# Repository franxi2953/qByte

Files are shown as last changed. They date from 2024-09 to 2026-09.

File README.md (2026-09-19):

> **Original GitLab repository:** This project was originally published in the [qByte directory of Open Bioeconomy Lab's RT-LAMP device repository](https://gitlab.com/open-bioeconomy-lab/diagnostics-hardware/rt-lamp-device/-/tree/master/qByte?ref_type=heads).

# qByte

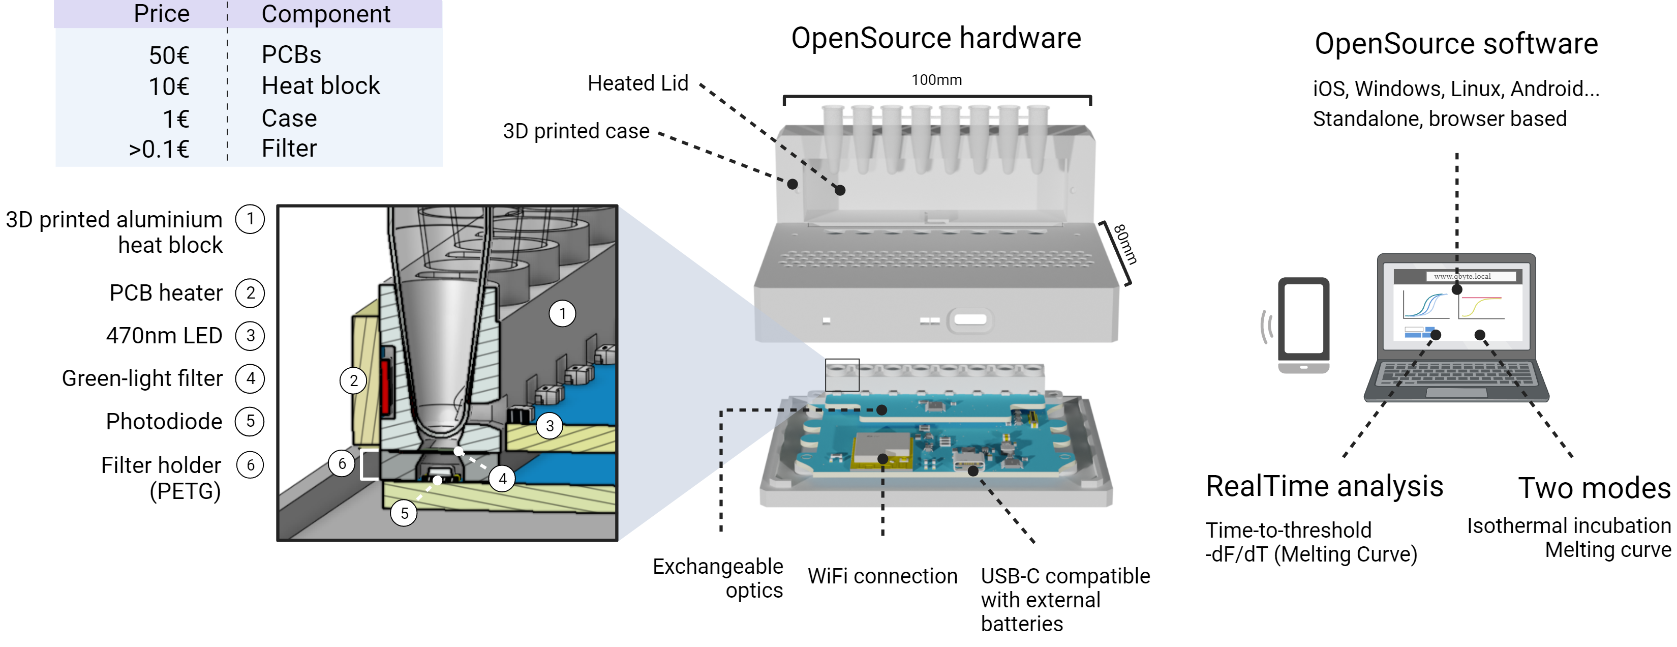
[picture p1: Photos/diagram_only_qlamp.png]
open_qLAMP


## Contents

- [Paper reference](#paper-reference)
- [Introduction](#introduction)
- [Quick start](#quick-start)
- [Making the device](#making-the-device)
- [Results](#results)
- [Components](#components)
  - [Costs](#costs)
  - [Electronics](#electronics)
  - [Code and firmware](#code-and-firmware)
  - [Case](#case)
- [Funding](#funding)
- [License](#license)

## Paper Reference

qByte: An open-source isothermal fluorimeter for democratizing analysis of nucleic acids, proteins and cells
Quero FJ, Aidelberg G, Vielfaure H, Huon de Kermadec Y, Cazaux S, et al. (2025) qByte: An open-source isothermal fluorimeter for democratizing analysis of nucleic acids, proteins and cells. PLOS Biology 23(5): e3003199. https://doi.org/10.1371/journal.pbio.3003199

## Introduction

Accessibility to scientific and diagnostic instrumentation is one of the main bottlenecks in the implementation of global health and decentralized science. The advancement of digital fabrication techniques and the cheapening of electronic prototyping have facilitated the emergence of open source prototypes that lower the cost of entry of these technologies. However, despite the importance of these prototypes for making the hands-on biotechnology more ubiquitous, they rarely move from the prototyping phase to their actual implementation, with their subsequent adaptation to mass production and validation in real scenarios. This is particularly relevant in the field of nucleic acid amplification, the gold standard in the field of diagnostics and biosensing. Despite relevant open-source products that allow nucleic acid amplification (as [PocketPCR](https://gaudi.ch/PocketPCR/) or [NinjaPCR](https://ninjapcr.tori.st/)) their results still require a subsequent analysis by electrophoresis gels or an end-point examination with a transilluminator. 

Here we describe the design and mid-scale production of the Open qLAMP, a device that, for a manufacturing cost of less than 50€, allows real-time detection of nucleic acid amplifications. We also include data that, together with our <2$ [in-house produced LAMP reactions](https://www.protocols.io/view/corona-detective-user-protocol-v2-0-14egnzbyqg5d/v2), validate the device for the detection of numerous targets, including SARS-CoV-2 clinical samples in resource constrained regions, presence of GMO elements in commercial food and the early detection of fungal infestation on chestnut plantations. Finally, we present results on how this system also has great potential in other fields such as enzyme activity characterization, protein production in cell-free extracts or antibiotic resistance screening in bacterial samples.

## Quick Start

This is a quick guide to follow if you received an already assembled and programmed qLAMP / qByte. For a complete assembly guide please follow the [making the device](#making-the-device) section.

1. Connect the device to your computer and open the [serial monitor in the Arduino IDE](https://docs.arduino.cc/software/ide-v2/tutorials/ide-v2-serial-monitor/) (other serial monitors should also work). At the moment, there are some plugins for the ESP32 (like the SPIFFS Filesystem Uploader Plugin) that are not yet supported on Arduino 2. As qByte uses the SPIFFS plugin, we recommend installing the legacy version 1.8.X 

2. Follow [these instructions](https://randomnerdtutorials.com/installing-the-esp32-board-in-arduino-ide-windows-instructions/) to download and install the esp32 board.

3. Ensure that the correct board and COM port are selected in the drop down at the top of screen, choose "Select Other Board and Port" if not. The board is DOIT ESP32 DEVKIT V1. If using a serial monitor other than the Arduino IDE it may _only_ be necessary to set the COM port number. If using Windows, you can find the COM port number by identifying the device in [Device Manager](https://www.lifewire.com/device-manager-2625860) > Ports (COM & LPT). It will be listed as Silicon Labs CP210x USB to UART Bridge. Instructions for finding the COM port on other operating systems can be found [here](https://www.mathworks.com/help/matlab/supportpkg/find-arduino-port-on-windows-mac-and-linux.html). If you don’t see the COM Port in your Arduino IDE, you need to install the [CP210x USB to UART Bridge VCP Drivers](https://www.silabs.com/products/development-tools/software/usb-to-uart-bridge-vcp-drivers).

4. Set the serial monitor to **115200 baud**. If the output is unreadable, verify the selected port and baud rate.

5. Configure the device's Wi-Fi by sending `wifi "ssid" "password"` (including the quotes) in the serial monitor. The device will restart and connect to that network. The network only needs internet access when checking for firmware updates.

6. Connect to the same Wi-Fi network on your computer or mobile device.

7. Open [http://qlamp.local](http://qlamp.local) in a browser. To change the local hostname, send `mDNS "new-name"` without the `.local` suffix. Send `mDNS` to display the current name.

8. The webpage should load within 30 seconds. If not, try reloading the page or changing the local network.

**Webpage Modes:**

```diff
1. Experiment Design:

   1. Assign conditions (e.g., negative/positive control, drug concentration) to each of the 8 tube strips.
   2. Assign colors to each condition.
   3. Experiment Run (two modes available):

```

```diff
2. Experiment Run:
   
   Control the parameters of the reaction and launch the protocol. 
   The device work in two different modes, which can be selected by a switch right above the "Run" button: 
   
   1. Normal Mode:
      1. Select time, temperature, space between readings, and heated lid temperature.
      2. Run the experiment as designed.
   2. Melting Curve Mode:
      1. Select time, temperature range, temperature increment, and time for each temperature step.
      2. The device will increase the temperature linearly.
      3. Run the experiment.
```

```diff
3. Analysis:

  Once the experiment is finished, you can download the data in a JSON file or .CSV file.
  Aditionally there are two implemented analysis options:

  1. Ct Value: Select a fluorescence threshold by clicking on the graph. The time for each sample to reach the threshold will be displayed.
  2. Melting curve: The graph will show the negative of the fluorescence change rate (-dF/dT) as a function of temperature.
```

```diff
4. Calibration:

  Reserved for sensor calibration (temperature and fluorescence).
  Observe resistance evolution of temperature sensors.
  Enter the actual temperature values measured with an external sensor.
  Download the data for further analysis.
```

Note: For any issues or questions, refer to the serial monitor for additional commands or consult the device's documentation.

## Making the Device

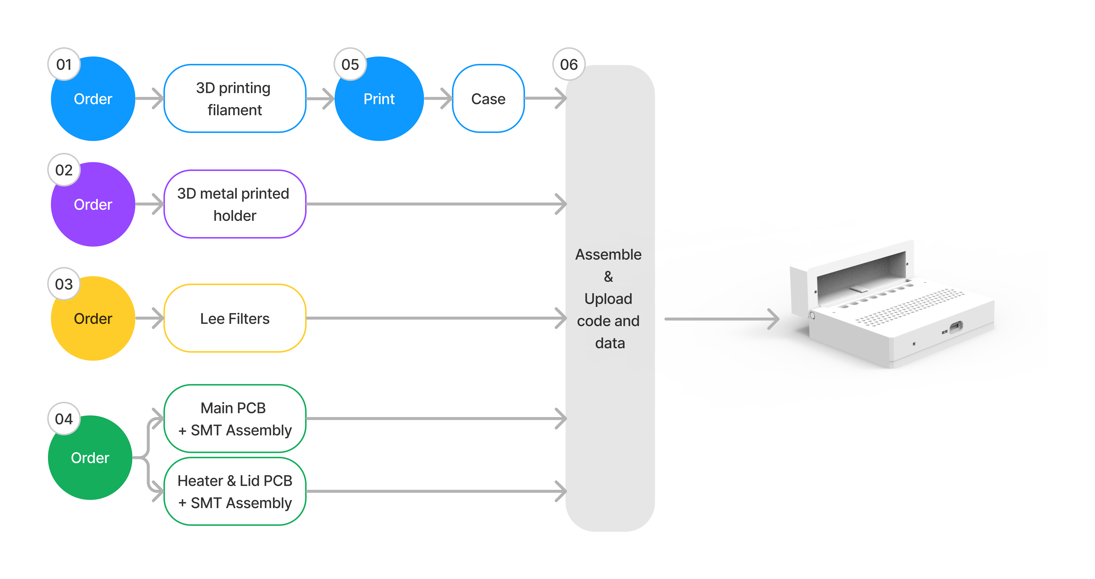
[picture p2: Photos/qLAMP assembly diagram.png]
Assembly


1. Assemble the device according to the blueprints in [Components](#components).

2. Install [PlatformIO Core](https://docs.platformio.org/en/latest/core/installation/index.html) or the [PlatformIO IDE extension](https://platformio.org/install/ide?install=vscode). PlatformIO supports Linux, Ubuntu, macOS, and Windows.

3. Build the firmware and SPIFFS interface from `Production/embedded system`:

   ```bash
   cd "Production/embedded system"
   pio run
   pio run --target buildfs
   ```

   [`platformio.ini`](Production/embedded%20system/platformio.ini) pins ESP32 Arduino 1.0.6 and loads the required device-specific libraries directly from [`libraries`](Production/embedded%20system/libraries).

4. Connect the ESP32-WROOM-32, which is configured as a DOIT ESP32 DEVKIT V1, and upload both images:

   ```bash
   pio run --target upload
   pio run --target uploadfs
   ```

   If Windows detects the CP210x serial adapter but WSL does not expose a `/dev/ttyUSB*` device, run PlatformIO or `esptool` on Windows, or attach the USB device to WSL with `usbipd`.

5. Follow the [quick start](#quick-start) section.

## Results
<details>
  <summary markdown="span">SARS-CoV-2 amplification with SYTO 9</summary>
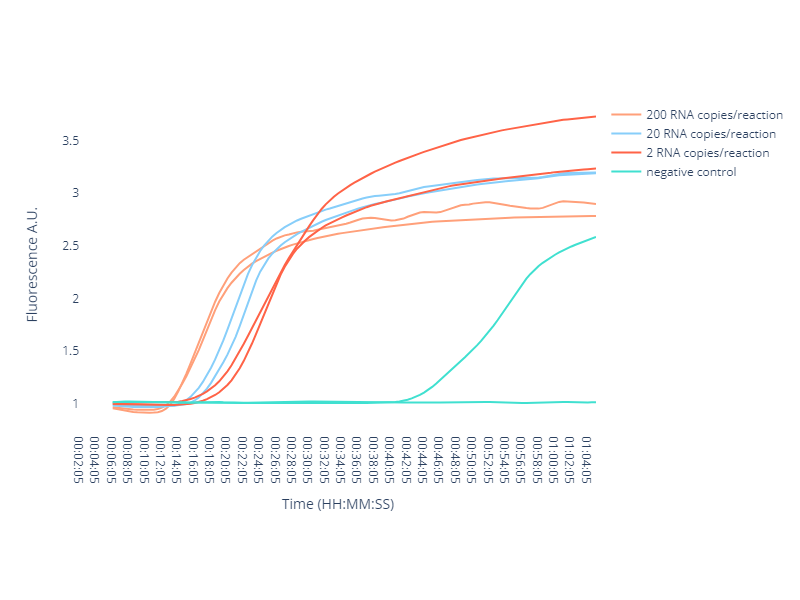
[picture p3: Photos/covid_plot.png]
    
</details>

<details>
  <summary markdown="span">Enzyme activity characterization with melting curve analysis</summary>
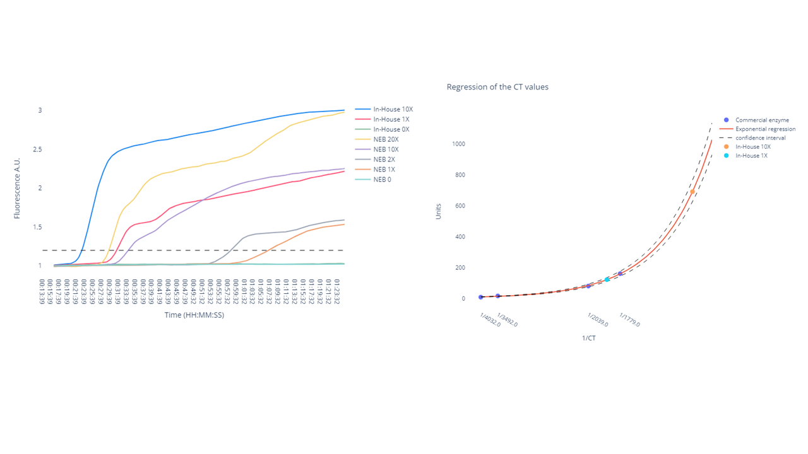
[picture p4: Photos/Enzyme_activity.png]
Enzyme activity
    
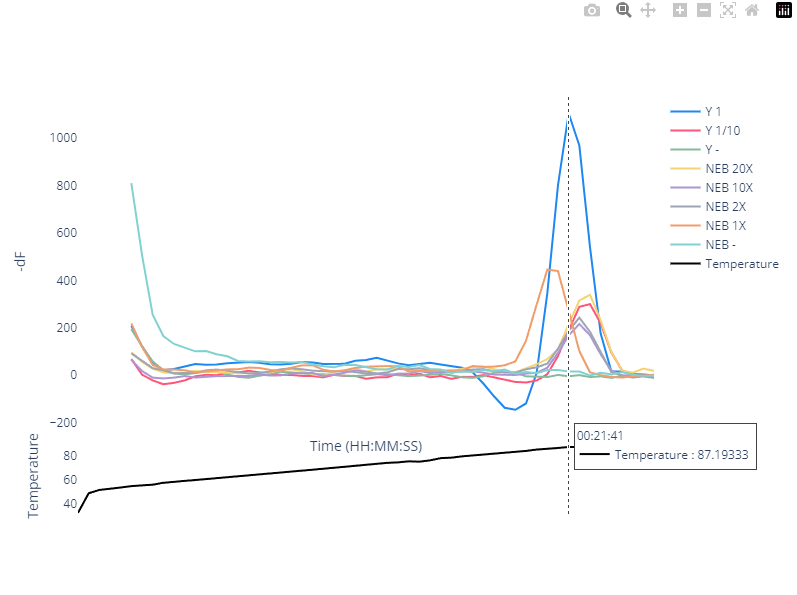
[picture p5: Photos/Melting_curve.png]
    
</details>

<details>
  <summary markdown="span">Fungal concentration detection in chestnut samples</summary>
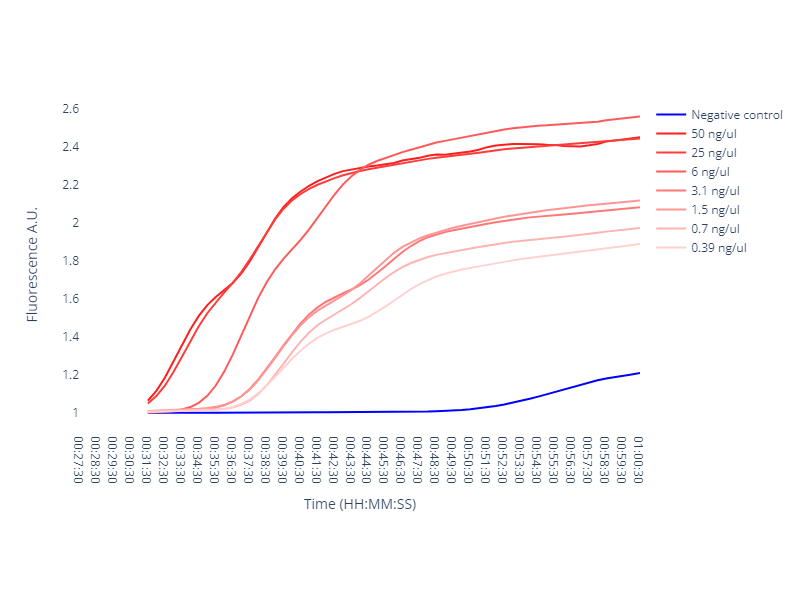
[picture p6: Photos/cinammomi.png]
    
</details>

<details>
  <summary markdown="span">Typhoid detection with CRISPR/Cas12</summary>
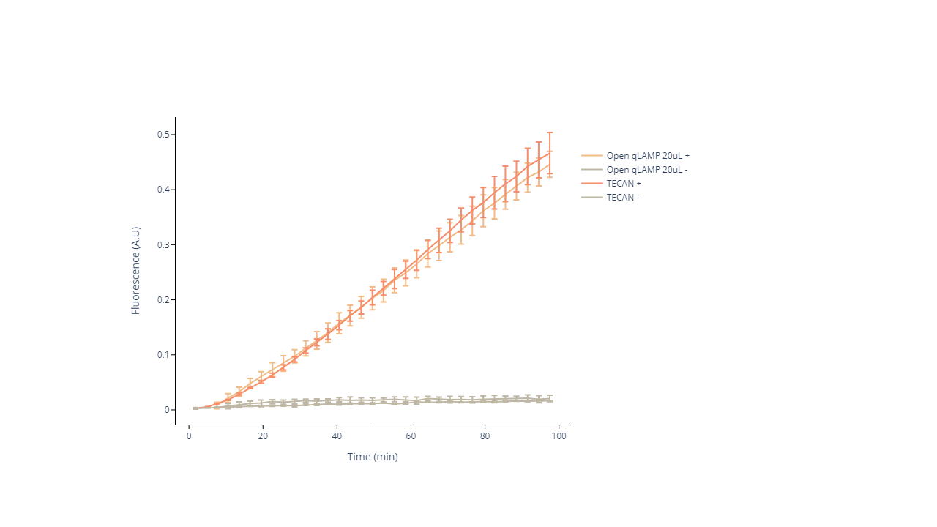
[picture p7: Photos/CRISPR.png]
    
</details>

## Components
### Costs

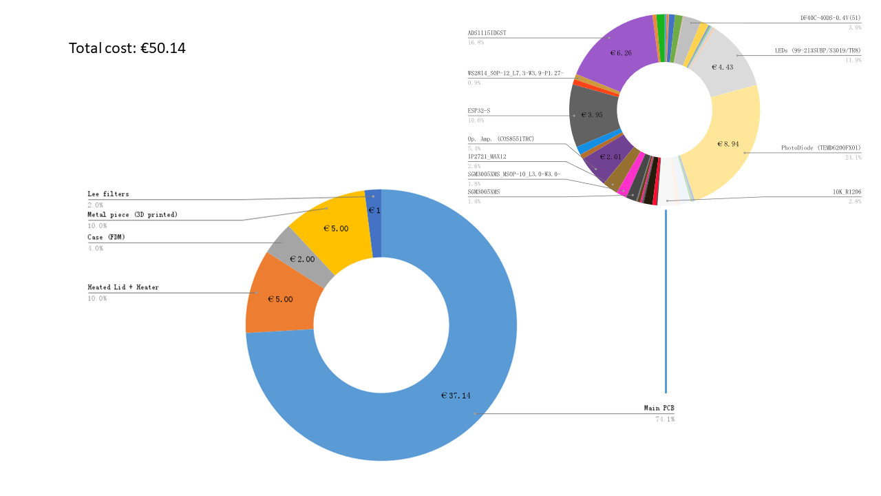
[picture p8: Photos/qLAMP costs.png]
Costs


### Electronics

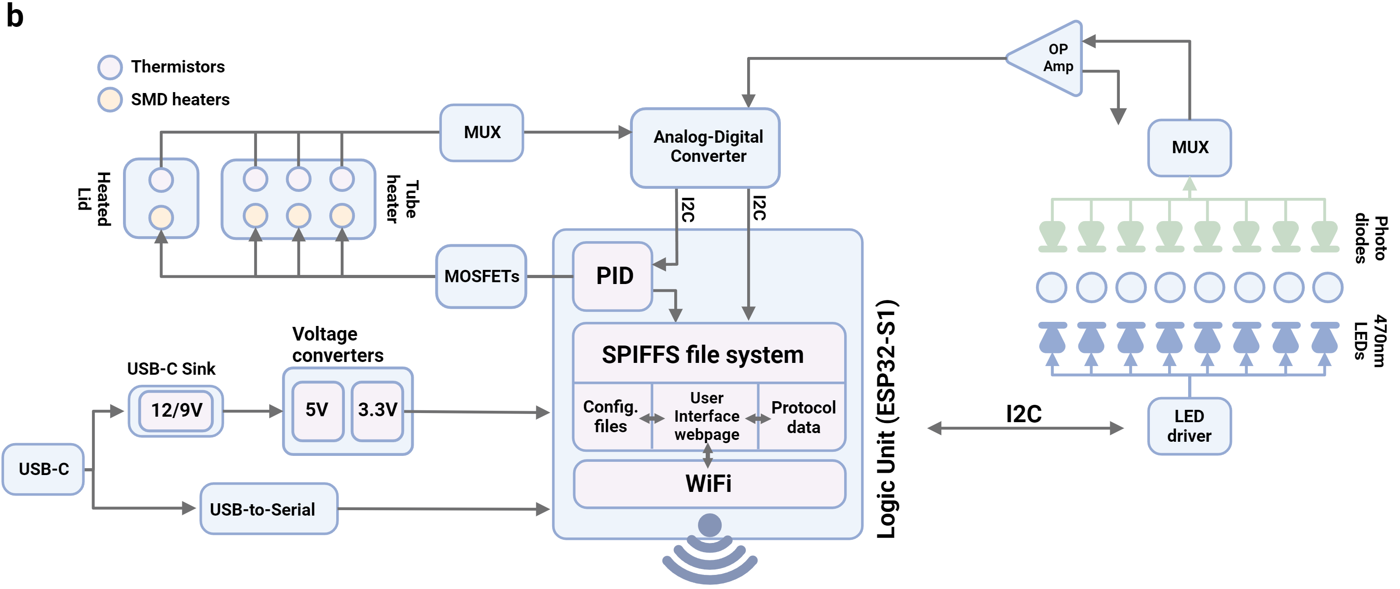
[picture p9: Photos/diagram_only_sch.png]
Electronics


Find them at [Open Source Hardware Lab](https://oshwlab.com/franxi2953/open-qlamp).

### Code and Firmware

The supported eight-well firmware is in [`Production/embedded system/code/main`](Production/embedded%20system/code/main). The separate [`Production/embedded system - 2 channel`](Production/embedded%20system%20-%202%20channel) directory is an experimental two-channel hardware variant.

- The ESP32 stores its web interface, configuration, protocols, and experiment data in [SPIFFS](https://randomnerdtutorials.com/install-esp32-filesystem-uploader-arduino-ide/).
- The device serves the interface at `http://<device-name>.local/` and at its assigned IP address.
- Wi-Fi and mDNS settings can be changed from the web interface or serial console.
- Firmware and interface updates can be started from the web interface or with the serial command `update`. Updates are published from this GitHub repository; see the [firmware update documentation](Production/embedded%20system/update_server/README.md).
- The HTTP control endpoints are documented in [`API_DOCUMENTATION.md`](Production/embedded%20system/API_DOCUMENTATION.md).

### Case

The latest version of the case can be found at the [OnShape Repository](https://cad.onshape.com/documents/fce8700b3c8f4038beef7327/w/66fbe211cbfcb16be40ce314/e/4a9a59be1c3a1e21a01af985?renderMode=0&uiState=627f9f3b91918f0016f76398). 

The following parts should be printed as follows:
- The "case_top" and the "cap" should be printed in PLA, one single piece, with 0.2mm of layer height. Be careful using an excess of supports or the hinge won't move.
- The "case_bottom" part should be printed in PLA. It can be printed with less precision than the previous part.
- The "intermediate" should be printed in PETG or any material with a glass transition of more than 63ºC. Lately we have started cutting it in black 1mm acrylic.

After printing/cutting the plastitc separator, with the help of some double side tape on the borders, attach a piece of [738 JAS Green Lee Filter](https://leefilters.com/colour/738-jas-green/) or [179 Chrome Orange Lee Filter](https://leefilters.com/colour/179-Chrome-Orange/) to filter the emiting light from the signal before the sensing unit.

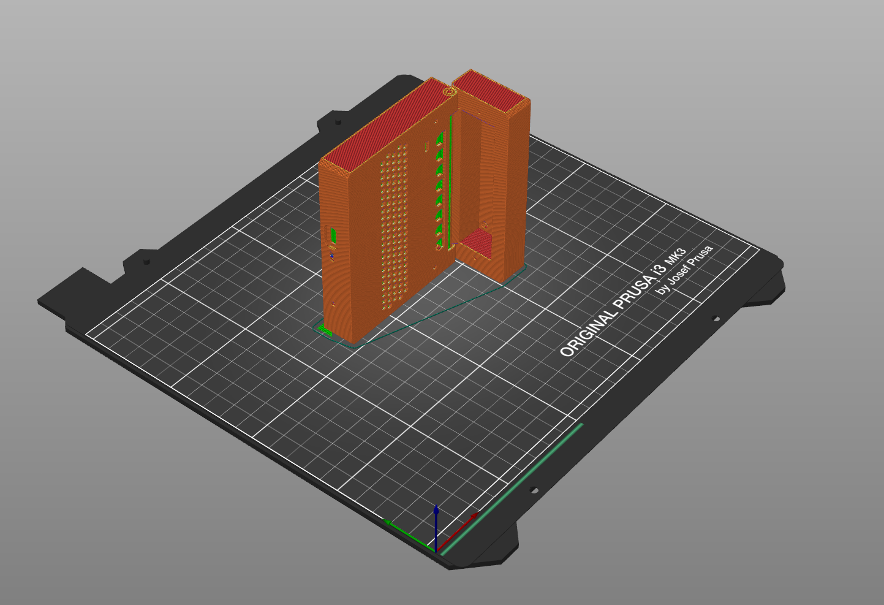
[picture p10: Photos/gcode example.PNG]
GCODE_example


## Funding
This project is funded by the Learning Planet Institute, the Tsinghua-Cambridge collaborative grant for Covid diagnosis and the Gathering for Open Science Hardware (GOSH) collaborative development funds 2022.

Thanks you all for making this possible!

## License

GCODE_example

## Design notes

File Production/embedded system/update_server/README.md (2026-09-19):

# qByte Firmware Updates

qByte updates are published through the Mac mini service at `qbyte.daicochiti.xyz`, with the public GitHub repository as the source of truth.

## Published Endpoints

- Manifest: `https://qbyte.daicochiti.xyz/update_server/data/fota.json`
- Firmware binary: `https://qbyte.daicochiti.xyz/binaries/main.ino.bin?v=<version>`
- Interface file list: `https://qbyte.daicochiti.xyz/update_server/file_list.json`
- Interface assets: `https://qbyte.daicochiti.xyz/code/main/data/<filename>`

The firmware checks the manifest only when an update is requested. It updates changed SPIFFS interface files first, then installs a newer firmware binary and restarts. An active experiment prevents updates.

## Device Controls

Open the device at `http://<device-name>.local/` and select **Update firmware**, or send `update` through the 115200-baud serial console. Keep the device powered during the download and restart.

Firmware `2.0.2` and earlier points to the retired `daicochiti.xyz` updater. Those devices need one USB flash to install `2.1.0`; subsequent releases can be installed from the web interface.

## Publishing a Release

1. Update `V_SOFTWARE` in `code/main/main.ino` and the version comment at the top of `code/main/data/index.html`.
2. Build the firmware and factory filesystem with PlatformIO using the configuration in the parent directory:

   ```bash
   pio run
   pio run --target buildfs
   ```

3. Copy `.pio/build/qbyte/firmware.bin` to `binaries/main.ino.bin` and `.pio/build/qbyte/spiffs.bin` to `binaries/main.spiffs.bin`. PlatformIO generates the bootloader, OTA metadata, and partition table when needed, so those generated files are not stored separately in this repository.
4. Add any changed interface assets to `file_list.json`. Keep `index.html` last so its version changes only after the supporting files install.
5. Update `data/fota.json` to the same firmware version, including the matching `?v=<version>` on the binary URL.
6. Push the release commit to `master`, deploy the update tree to the Mac mini, and verify each public endpoint.

The current OTA library does not verify firmware signatures. Only publish reviewed binaries, and treat write access to `master` as release access.

## Server

The production `launchd` service runs:

```bash
python3 server.py 8003 ../
```

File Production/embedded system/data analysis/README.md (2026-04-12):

# qByte Data Analysis (Offline, Phaser UI)

This folder contains an offline web app with a Phaser-based interface to analyze `Processed Fluo` CSV files.

## Main Features

- Offline operation with local libraries in `vendor/`:
  - `phaser.min.js`
  - `chart.umd.min.js`
  - `papaparse.min.js`
- Phaser loading scene + main scene
- Foldable side panels (left/right)
- Tabs:
  - `Processed Fluo`: only the 8 fluorescence tubes
  - `Melting`: `-dF/dT` computed from fluorescence derivative over temperature derivative
- Sample editor (left panel):
  - Per-tube sample name
  - Per-tube color
  - Palette presets (`macOS`, `Viridis`, `Plasma`, `Ocean`)
- Melting controls (right panel):
  - Temperature channel selector
  - Analysis range (%)
  - Smoothing window
- CSV export for active tab

## Expected CSV Format

1. First column: `Time`
2. Middle columns: fluorescence channels (first 8 are used)
3. Last 5 columns: temperature channels (including target temperature)

This is compatible with the `Processed Fluo` export generated by the qByte UI.

## Run

Open `index.html` in a browser.

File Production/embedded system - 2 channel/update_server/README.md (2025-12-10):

# Firmware Update Server

This directory contains the firmware update server for the qByte LAMP device.

## Directory Structure

```
update_server/
├── data/                    # Web interface and firmware files
│   ├── index.html          # Main web interface
│   ├── style.css           # CSS styles
│   ├── functions.js        # JavaScript functions
│   ├── data_query.js       # Data query functions
│   ├── analysis.js         # Analysis functions
│   ├── JS_merged.js.gz     # Compressed JavaScript
│   ├── uikit.min.css.gz    # Compressed CSS framework
│   ├── config.txt          # Default configuration
│   ├── credentials.txt     # Default credentials
│   ├── last_run.txt        # Last run data
│   ├── protocols.txt       # Protocol definitions
│   ├── main.ino.bin        # Firmware binary
│   └── fota.json           # Firmware update manifest
├── file_list.json          # List of files to update
├── server.py               # Python HTTPS server
├── start_server.sh        # Startup script
└── README.md              # This file
```

## Setup Instructions

1. **Copy to Raspberry Pi**: Upload the entire `update_server` directory to your Raspberry Pi.

2. **SSL Certificates (Recommended)**: For secure HTTPS, generate SSL certificates:
   ```bash
   openssl req -x509 -newkey rsa:4096 -keyout key.pem -out cert.pem -days 365 -nodes
   ```

3. **Start the Server**:
   ```bash
   cd update_server
   ./start_server.sh
   ```

   Or manually:
   ```bash
   python3 server.py 443 .
   ```

## Server Configuration

- **Default Port**: 443 (HTTPS) or 80 (HTTP if no certificates)
- **Host**: Should be accessible at `daicochiti.xyz`
- **Endpoints**:
  - `/data/fota.json` - Firmware update manifest
  - `/data/main.ino.bin` - Firmware binary
  - `/file_list` - List of files to update
  - `/data/<file>` - Individual web interface files

## Security Notes

- The server includes CORS headers for cross-origin requests
- HTTPS is strongly recommended for production use
- Ensure the server is only accessible from trusted networks

## Updating Firmware

1. Replace `data/main.ino.bin` with the new firmware binary
2. Update the version in `data/fota.json`
3. Update `file_list.json` if new files are added
4. Restart the server

The ESP32 device will automatically check for updates and download new firmware when available.

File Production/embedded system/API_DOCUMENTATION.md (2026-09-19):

# RT-LAMP Device API Documentation

## Overview
This API allows remote control and monitoring of an RT-LAMP thermal cycling device via HTTP requests. The device runs a web server that exposes various endpoints for experiment control, temperature management, fluorescence reading, and configuration.

## Connection

### Base URL
- **IP Address**: `http://<device-ip>/`
- **mDNS**: `http://<device-mdns>.local/`

The device IP and mDNS name are printed to serial console on successful WiFi connection. By default this is: http://qbyte.local. In case mDNS do not work you can use the IP address assigned to the device as a safe fallback option.

If the device do not find the local network it was configured to connect to, it will create a WiFi Access Point named "qByte-Setup". You can connect to this AP and access the configuration portal at http://qbyte.local or http://192.168.4.1. In wuch a portal you can configure a new wifi network for the device to connect to. You can also do this via serial commands, sending 'wifi "ssid" "password"' (with " included) via a serial terminal working at 115200 baud rate.

Remember that the USB serial wire connected to a laptop is only required for initial configuration. Once the device is connected to a WiFi network, all interactions should be done wirelessly and the device should be powered by its USB-C 12V charger.

### Authentication
Currently, no authentication is required.

---

## API Endpoints

### 1. Device Status & Information

#### GET `/OnGoing`
Check if an experiment is currently running.

**Response:**
- `1` - Experiment is running
- `0` - No experiment running

**Example:**
```bash
GET http://device-ip/OnGoing
```

---

#### GET `/free_memory`
Get available SPIFFS storage space percentage (this is used to store the current protocol data and is erased once a new protocol starts).

**Response:**
- Text: Percentage of free SPIFFS space

**Example:**
```bash
GET http://device-ip/free_memory
```

---

### 2. Temperature Control

#### GET `/temp`
Get current temperature of WELL1 (which is supposed to be a proxy of all wells).

**Response:**
- Text: Temperature value with 4 decimal places (e.g., `25.1234`)

**Example:**
```bash
GET http://device-ip/temp
```

---

#### GET `/new_temp?degrees=<value>`
Set new target temperature for the heating wells.

**Parameters:**
- `degrees` (required): Target temperature in Celsius (0-100°C)

**Response:**
- Success: `TARGET TEMPERATURE SET TO <value>ºC`
- Error: `[ERROR] TEMPERATURE NOT IN RANGE [0ºC-100ºC]`
- Error: `[ERROR] TARGET TEMPERATURE REQUIRED`

**Example:**
```bash
GET http://device-ip/new_temp?degrees=65
```

---

#### GET `/lid_temp`
Get or set lid temperature.

**Parameters:**
- `set` (optional): New lid temperature in Celsius

**Response:**
- Without `set`: Current lid temperature
- With `set`: `[OK] LID TEMPERATURE CHANGED TO <value>ºC`

**Examples:**
```bash
# Get current lid temperature
GET http://device-ip/lid_temp

# Set lid temperature to 105°C
GET http://device-ip/lid_temp?set=105
```

---

#### GET `/lid_diff`
Get or set lid temperature difference threshold.

**Parameters:**
- `set` (optional): New lid temperature difference value in Celsius

**Response:**
- Without `set`: Current lid temperature difference
- With `set`: `[OK] LID TEMPERATURE DIFFERENCE CHANGED TO <value>ºC`

**Examples:**
```bash
# Get current difference
GET http://device-ip/lid_diff

# Set difference to 5°C
GET http://device-ip/lid_diff?set=5
```

---

### 3. Protocol Execution

#### GET `/Run?degrees=<value>`
Start a new thermal cycling protocol at specified temperature.

**Parameters:**
- `degrees` (required): Target temperature in Celsius

**Response:**
- Success: `[OK] STARTING NEW PROTOCOL AT <value>ºC`
- Error: `[ERROR] TARGET TEMPERATURE REQUIRED`

**Side Effects:**
- Resets all variable gains to 0
- Creates/overwrites `/last_run.txt` file
- Sets `OnGoing` flag to true

**Example:**
```bash
GET http://device-ip/Run?degrees=65
```

---

#### GET `/RunMelting`
Start a melting curve analysis protocol.

**Response:**
- `[OK] STARTING NEW MELTING CURVE`

**Side Effects:**
- Creates/overwrites `/last_run.txt` file
- Sets `OnGoing` and `OnGoingMelting` flags to true
- Uses temperature range from `melting_range` configuration

**Example:**
```bash
GET http://device-ip/RunMelting
```

---

#### GET `/Stop`
Stop the currently running protocol.

**Response:**
- `[OK] STOPPING PROTOCOL`

**Side Effects:**
- Sets target temperature to 0
- Writes "stop" to `/last_run.txt`
- Clears `OnGoing` flag

**Example:**
```bash
GET http://device-ip/Stop
```

---

#### GET `/manual_cycle`
Force an immediate thermal cycle and fluorescence reading, bypassing the normal cycle time interval. This is useful when you want to take a reading immediately without waiting for the scheduled cycle time.

**Response:**
- Success: `[OK] STARTING MANUAL CYCLE`
- Error: `[ERROR] PROTOCOL NOT RUNNING`

**Side Effects:**
- Triggers an immediate cycle regardless of cycle_time setting
- Automatically performs fluorescence reading as part of the cycle
**Example:**
```bash
GET http://device-ip/manual_cycle
```

---

### 4. Fluorescence Reading

#### GET `/ReadFluo`
Request a fluorescence measurement to be taken. This sets a flag that tells the device to perform a fluorescence reading on the next sensor update cycle. Use this when you want to take a standalone fluorescence measurement without running a full protocol cycle.

**Response:**
- `[OK] READING FLUORESCENCE`

**Side Effects:**
- Sets `reading_fluorescence` flag to true
- Device will perform the reading asynchronously on next sensor update

**Note:** This is different from `/manual_cycle` which triggers a full thermal cycle. Use `/ReadFluo` for quick fluorescence checks without re running the PID. In reality, both are quite equivalent and just differ slightly in timing, which is useful for debug. Normally use the manual_cycle as for protocol runs is safer.

**Example:**
```bash
GET http://device-ip/ReadFluo
```

---

#### GET `/fluo`
Retrieve the most recent fluorescence measurement values from all 8 channels. This returns cached data from the last reading (triggered by either `/ReadFluo`, `/manual_cycle`, or automatic cycle during a running protocol).

**Response:**
- Text: Comma-separated fluorescence values for all 8 channels

**Note:** This endpoint only retrieves stored values - it does not trigger a new reading. Call `/ReadFluo` first if you need fresh data.

**Example:**
```bash
# Workflow: Request reading, wait briefly, then retrieve values
GET http://device-ip/ReadFluo
# Wait ~1-2 seconds for reading to complete
GET http://device-ip/fluo
# Response example: 1234.5,2345.6,3456.7,4567.8,5678.9,6789.0,7890.1,8901.2
```

---

### 5. Calibration

#### GET `/Calibration`
Start calibration procedure.

**Response:**
- `[OK] CALIBRATION STARTED`

**Side Effects:**
- Sets `calibrate` flag to true
- Calibration may take approximately 1 minute

**Example:**
```bash
GET http://device-ip/Calibration
```

---

#### GET `/readWeights`
Get calibration weight values.

**Response:**
- Text: Comma-separated list of 8 weight values

**Example:**
```bash
GET http://device-ip/readWeights
# Response: 1.234,5.678,9.012,3.456,7.890,1.234,5.678,9.012
```

---

#### GET `/weights`
Get calibration weight values (alternative endpoint).

**Response:**
- Text: Comma-separated list of 8 weight values

**Example:**
```bash
GET http://device-ip/weights
```

---

### 6. Data Retrieval

#### GET `/data_request`
Get current experiment data.

**Response:**
- Success: Contents of `/last_run.txt` file
- Error: `[ERROR] NO PROTOCOL RUNNING` (if no protocol is running and last one already retrieved)

**Example:**
```bash
GET http://device-ip/data_request
```

---

#### GET `/last_run_request`
Get data from the last completed run.

**Response:**
- Contents of `/last_run.txt` file

**Example:**
```bash
GET http://device-ip/last_run_request
```

---

### 7. Configuration Parameters

#### GET `/cycle_time`
Get or set cycle time in milliseconds.

**Parameters:**
- `set` (optional): New cycle time in milliseconds

**Response:**
- Without `set`: Current cycle time value
- With `set`: `[OK] CYCLE TIME CHANGED TO <value>ms`

**Examples:**
```bash
# Get current cycle time
GET http://device-ip/cycle_time

# Set cycle time to 30000ms (30 seconds)
GET http://device-ip/cycle_time?set=30000
```

---

#### GET `/melting_step`
Get or set temperature step for melting curve.

**Parameters:**
- `set` (optional): New melting step in Celsius

**Response:**
- Without `set`: Current melting step value
- With `set`: `[OK] MELTING STEP CHANGED TO <value>ºC`

**Examples:**
```bash
# Get current melting step
GET http://device-ip/melting_step

# Set melting step to 0.5°C
GET http://device-ip/melting_step?set=0.5
```

---

#### GET `/melting_time`
Get or set time per step for melting curve.

**Parameters:**
- `set` (optional): New melting time in milliseconds

**Response:**
- Without `set`: Current melting time value
- With `set`: `[OK] MELTING TIME CHANGED TO <value>ms`

**Examples:**
```bash
# Get current melting time
GET http://device-ip/melting_time

# Set melting time to 5000ms
GET http://device-ip/melting_time?set=5000
```

---

#### GET `/melting_range`
Get or set temperature range for melting curve [start, end].

**Parameters:**
- `set` (optional): New melting range as "start,end" (e.g., "60,95")

**Response:**
- Without `set`: Current range as "start,end"
- With `set`: `[OK] MELTING RANGE CHANGED TO <range>ºC`

**Examples:**
```bash
# Get current melting range
GET http://device-ip/melting_range
# Response: 60,95

# Set melting range from 60°C to 95°C
GET http://device-ip/melting_range?set=60,95
```

---

### 8. Protocol Library Management

#### GET `/protocols`
Retrieve all saved protocols.

**Response:**
- JSON object containing all saved protocols

**Example:**
```bash
GET http://device-ip/protocols
```

---

#### GET `/protocols?save_new=1&name=<protocol_name>&protocol_data=<json_data>`
Save a new protocol to the library.

**Parameters:**
- `save_new`: Must be set to `1`
- `name` (required): Protocol name
- `protocol_data` (required): JSON-encoded protocol data

**Response:**
- Success: `[OK] Protocol saved successfully`
- Error: `[ERROR] Invalid protocol data format`
- Error: `[ERROR] Protocol name is required`
- Error: `[ERROR] Failed to open protocols file for writing`

**Example:**
```bash
GET http://device-ip/protocols?save_new=1&name=MyProtocol&protocol_data={"temp":65,"cycles":40}
```

---

#### GET `/protocols?delete=1&name=<protocol_name>`
Delete a protocol from the library.

**Parameters:**
- `delete`: Must be set to `1`
- `name` (required): Protocol name to delete

**Response:**
- Success: `[OK] Protocol deleted successfully`
- Error: `[ERROR] Protocol not found`
- Error: `[ERROR] Failed to parse existing protocols`

**Example:**
```bash
GET http://device-ip/protocols?delete=1&name=MyProtocol
```

---

### 9. Diagnostics

#### GET `/res`
Get resistance measurement.

**Response:**
- Text: Resistance value

**Example:**
```bash
GET http://device-ip/res
```

---

#### GET `/variable_gains`
Get variable gain values for all 8 channels.

**Response:**
- Text: Comma-separated list of 8 gain values

**Example:**
```bash
GET http://device-ip/variable_gains
# Response: 0,0,0,0,0,0,0,0
```

---

#### GET `/led_trial`
Test LED functionality (cycles through all 8 LEDs).

**Response:**
- `ok`

**Side Effects:**
- Sequentially turns on each LED for 500ms

**Example:**
```bash
GET http://device-ip/led_trial
```

---

### 10. Device Configuration and Updates

#### GET `/device-config`
Read the device IP address, mDNS name, Wi-Fi SSID, and saved interface theme. The saved Wi-Fi password is never returned.

**Response:** JSON with `ip`, `mdns`, `ssid`, and `theme` fields.

#### GET `/device-config?theme=<theme>`
Save the interface theme without restarting the device. Supported values are `tokyo-night`, `catppuccin`, `nord`, and `sunset`.

#### GET `/device-config?save=1&mdns=<name>&ssid=<ssid>&password=<password>`
Save Wi-Fi and mDNS settings and restart the device.

Send `mdns`, `ssid`, and `password` as query parameters. Leave `password` empty to keep the existing password.

```bash
curl 'http://device-ip/device-config?save=1&mdns=qbyte&ssid=my-network&password=my-secret'
```

#### GET `/firmware-update`
Read the installed firmware version and update state.

**Response:** JSON with `version`, `manifest`, `updating`, and `experiment_running` fields.

#### GET `/firmware-update?start=1`
Start a firmware and web-interface update from the GitHub manifest. The device must have internet access and no experiment may be running. The endpoint returns `202` and the update continues after the response is sent.

```bash
curl 'http://device-ip/firmware-update?start=1'
```

The manifest URL used by the current firmware is:
`https://qbyte.daicochiti.xyz/update_server/data/fota.json`

---

## Common Workflows

### Starting an Experiment
```bash
# 1. Check if device is ready
GET http://device-ip/OnGoing
# Should return: 0

# 2. Set desired temperature and start protocol
GET http://device-ip/Run?degrees=65

# 3. Monitor progress
GET http://device-ip/data_request
```

### Running a Melting Curve
```bash
# 1. Configure melting parameters (optional)
GET http://device-ip/melting_range?set=60,95
GET http://device-ip/melting_step?set=0.5
GET http://device-ip/melting_time?set=5000

# 2. Start melting curve
GET http://device-ip/RunMelting

# 3. Monitor progress
GET http://device-ip/data_request
```

### Stopping an Experiment
```bash
GET http://device-ip/Stop
```

### Reading Temperature and Fluorescence
```bash
# Get current temperature
GET http://device-ip/temp

# Trigger fluorescence reading
GET http://device-ip/ReadFluo

# Wait a moment, then retrieve values
GET http://device-ip/fluo
```

---

## Notes

1. **All endpoints use HTTP GET requests.** Writes use query parameters because this firmware's legacy AsyncWebServer stack does not reliably process request bodies.
2. **Configuration changes are persisted** - Settings like cycle_time, lid_temp, melting parameters are saved to device storage
3. **Protocol data is stored in SPIFFS** - The `/last_run.txt` file contains experiment data
4. **No concurrent experiments** - Only one protocol can run at a time
5. **Response format** - Most responses are plain text, protocol library uses JSON format but sent in plain text
6. **Temperature units** - All temperatures are in Celsius
7. **Time units** - Cycle and melting times are in milliseconds

---

## Error Handling

The API returns HTTP 200 status for most requests, with error messages in the response body starting with `[ERROR]`. Success messages start with `[OK]`.

Common error patterns:
- Missing required parameters: `[ERROR] TARGET TEMPERATURE REQUIRED`
- Invalid ranges: `[ERROR] TEMPERATURE NOT IN RANGE [0ºC-100ºC]`
- Invalid state: `[ERROR] NO PROTOCOL RUNNING`
- File system errors: `[ERROR] Failed to open protocols file for writing`

---

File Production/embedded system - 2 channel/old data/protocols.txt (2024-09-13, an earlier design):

{
  "Duplicates": {
    "samples": {
      "Neg":["#1E87F0",[0,1]],
      "Pos":["#FF5579",[2,3]],
      "Sample 1":["#87ba9d",[4,5]],
      "Sample 2":["#F5D372",[6,7]]
    }
  },
  "Individual": {
    "samples": {
      "Neg":["#1E87F0",[0]],
      "Pos":["#FF5579",[1]],
      "Sample 1":["#87ba9d",[2]],
      "Sample 2":["#F5D372",[3]],
      "Sample 3":["#AB96D2",[4]],
      "Sample 4":["#9CA5B5",[5]],
      "Sample 5":["#F09D6C",[6]],
      "Sample 6":["#7FD2D1",[7]]
    }
  }
}

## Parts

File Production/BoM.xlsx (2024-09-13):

Part | Description | Quantity (Per device) | Total Price (Mid scale) | Example supplier | Lead Time | Example Link
Main PCBs | Main PCB + LED module (Plus assembly) | 1 | 40$ | PCBWay | 5-6 days | https://www.pcbway.com/
Flexible PCBs | Heater + heating lid (Plus assembly) | 1 | 15$ | PCBWay | 7-8 days | https://www.pcbway.com/ | Electronics
Top case with lid | Printed in PLA | 1 | 10$ | PCBWay | 7-8 days | https://www.pcbway.com/ | 3D printing
Bottom case | Printed in PLA | 1 | 5$ | PCBWay | 7-8 days | https://www.pcbway.com/ | Others
Intermidiate part | Printed in PETG | 1 | 2$ | PCBWay | 7-8 days | https://www.pcbway.com/
Tube holder | Printed in alluminium (AlSi10Mg) | 1 | 5$ | PCBWay | 8-9 days | https://www.pcbway.com/
M3 inserts & screws | To assemble the case | 4 | <1$ | Aliexpress | 15 days | https://es.aliexpress.com/item/1005006589893189.html
738 LEE Filter™ | To filter the signal | 1 | <1$ | LEE | Depends on region | https://leefilters.com/colour/738-jas-green/
Heat resistant tape | To stick the heater to the holder | 1 | <1$ | Aliexpress | 15 days | https://es.aliexpress.com/item/1005004220389088.html
Silicone Foam 3mm | To press the heating lid vs the tubes | 1 | <1$ | Aliexpress | 15 days | https://es.aliexpress.com/item/1005006922115651.html
Magnets | To ensure the lid does not open | 2 | <1$ | Aliexpress | 15 days | https://es.aliexpress.com/item/1005004837777482.html
 | (With commercial 3D print) Total price |  | 77$
 | (Self-printed) Total price |  | 60$

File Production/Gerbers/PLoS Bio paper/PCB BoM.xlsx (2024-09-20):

No. | Quantity | Device | Designator | Footprint | Value | Manufacturer Part | Manufacturer | Supplier Part | Supplier | LCSC Price | LCSC Stock | Final price/unit | Total price | Total number needed | Notes
1 | 1 | 1uF | C1 | C0805 |  | 0805B105K500NT | Guangdong Fenghua Advanced Tech | C215803 | LCSC | 0.0101 | 1211514 | 0.0101 | 0.0505 | 5 | FEEL FREE TO ADAPT ALL RESISTORS AND CAPACITORS TO CHEAPER ONES IN THE ASSEMBLY LINE
2 | 1 | 10uF | C2 | C0805 |  | CL21A106KOQNNNE | SAMSUNG | C1713 | LCSC |  |  |  | 0.53 | 5 | Buy 50 and keep it for future orders
3 | 3 | CL05B104KO5NNNC | C3,C15,C34 | C0402_NEW | 100nF | CL05B104KO5NNNC | SAMSUNG(三星) | C1525 | LCSC |  |  |  | 0.1 | 15 | Buy 100 and keep it for future orders
4 | 1 | 10uF_CAP-SMD_L3.2-W1.6-R-RD | C7 | CAP-SMD_L3.2-W1.6-R-RD |  | TAJA106K016RNJ | AVX | C7171 | LCSC |  |  |  | 1.37 | 5 | Buy 15 units
5 | 1 | 100nF_C0402(1) | C9 | C0402 |  | CC0402KRX7R7BB104 | YAGEO | C60474 | LCSC |  |  |  | 0.09 | 5 | Buy 100 and keep it for future orders
6 | 2 | CL10A106MA8NRNC | C16,C38 | C0603 | 10uF | CL10A106MA8NRNC | SAMSUNG(三星) | C96446 | LCSC | 0.0237 | 2118185 | 0.0474 | 0.237 | 10
7 | 1 | CC0603KRX7R9BB104 | C17 | C0603 | 100nF | CC0603KRX7R9BB104 | YAGEO(国巨) | C14663 | LCSC |  |  |  | 0.24 | 5 | Buy 100 and keep it for future orders
8 | 2 | CL21A226MAQNNNE_C45783 | C18,C19 | C0805 | 22uF | CL21A226MAQNNNE | SAMSUNG(三星) | C45783 | LCSC |  |  |  | 0.53 | 10 | Buy 20 and keep it for future orders
9 | 1 | 100nF_C0402 | C25 | C0402 |  | VJ0402G104KXQCW1BC | Vishay Intertech | C169292 | LCSC | 0.0063 | 1134950 | 0.0063 | 0.0315 | 5
10 | 1 | CL10A106KP8NNNC | C26 | C0603 | 10uF | CL10A106KP8NNNC | SAMSUNG(三星) | C19702 | LCSC |  |  |  | 0.67 | 5 | Buy 100 and keep it for future orders
11 | 1 | CL10C331JB8NNNC | C35 | C0603 | 330pF | CL10C331JB8NNNC | SAMSUNG(三星) | C1664 | LCSC |  |  |  | 0.76 | 5 | Buy 100 and keep it for future orders
12 | 1 | CL21A476MQYNNNE | C36 | C0805 | 47uF | CL21A476MQYNNNE | SAMSUNG(三星) | C16780 | LCSC |  |  |  | 0.46 | 5 | Buy 20 and keep it for future orders
13 | 1 | CL21B105KBFNNNE | C37 | C0805 | 1uF | CL21B105KBFNNNE | SAMSUNG(三星) | C28323 | LCSC |  |  |  | 0.48 | 5 | Buy 50 and keep it for future orders
14 | 1 | CL31A107MQHNNNE | C39 | C1206 | 100uF | CL31A107MQHNNNE | SAMSUNG(三星) | C15008 | LCSC |  |  |  | 0.31 | 5
15 | 2 | DF40C-40DP-0.4V(51) | CN2,CN3 | CONN-SMD_DF40C-40DP-0.4V |  | DF40C-40DP-0.4V(51) | HRS(广濑) | C424643 | LCSC | 0.39 | 888 | 0.78 | 3.9 | 10
16 | 1 | DF40C-40DS-0.4V(51) | CN4 | CONN-SMD_DF40C-40DS-0.4V51 |  | DF40C-40DS-0.4V(51) | HRS(广濑) | C424644 | LCSC | 0.36 | 8823 | 0.36 | 1.8 | 5
17 | 1 | BM22-4S-V(51) | CN6 | CONN-SMD_BM22-4S-V-51 |  | BM22-4S-V(51) | HRS(广濑) | C424630 | LCSC |  | 12755 |  | 0.89 | 5
18 | 1 | YNR4030-4R7M | L1 | IND-SMD_L4.0-W4.0 | 4.7uH | YNR4030-4R7M | YJYCOIN(益嘉源) | C340391 | LCSC |  |  |  | 0.59 | 5 | Buy 10 and keep it for future orders
19 | 1 | 19-217/BHC-ZL1M2RY/3T | LED1 | LED0603-R-RD |  | 19-217/BHC-ZL1M2RY/3T | EVERLIGHT | C72041 | LCSC |  |  |  | 0.36 | 5 | Buy 20 and keep it for future orders
20 | 1 | 19-217/Y5C-AM1N1VY/3T | LED2 | LED0603-R-RD |  | 19-217/Y5C-AM1N1VY/3T | Everlight Elec | C282130 | LCSC | 0.0235 | 48080 | 0.0235 | 0.1175 | 5
21 | 1 | 19-217/GHC-YR1S2/3T | LED3 | LED0603-R-RD |  | 19-217/GHC-YR1S2/3T | EVERLIGHT | C72043 | LCSC |  |  |  | 0.54 | 5 | Buy 20 and keep it for future orders
22 | 8 | 99-213SUBP/S3019/TR8 | LED4,LED5,LED6,LED7,LED8,LED9,LED10,LED11 | LED-SMD_L2.5-W1.2-RD |  | 99-213SUBP/S3019/TR8 | EVERLIGHT(台湾亿光) | C264616 | LCSC | 0.1325 | 1560 | 1.06 | 5.3 | 40
23 | 1 | TEMD6200FX01 | PD1 | LED0805-RD |  | TEMD6200FX01 | Vishay Intertech | C499517 | LCSC | 0.8639 | 80 | 0.8639 | 4.3195 | 5
24 | 7 | TEMD6200FX01_LED0805-RD | PD2,PD3,PD4,PD5,PD6,PD7,PD8 | LED0805-RD |  | TEMD6200FX01 | Vishay Intertech | C499517 | LCSC | 0.8639 | 80 | 6.0473 | 30.2365 | 35
25 | 1 | AO3400A_C344010_SOT-23_L2.9-W1.3-P1.90-LS2.4-BR | Q2 | SOT-23_L2.9-W1.3-P1.90-LS2.4-BR |  | AO3400A | Bourne Semicon (Shenzhen) | C344010 | LCSC |  |  |  | 0.4 | 5 | Buy 10 and keep it for future orders
26 | 1 | LMBT3904DW1T1G | Q5 | SOT-363_L2.0-W1.3-P0.65-LS2.1-TL |  | LMBT3904DW1T1G | LRC | C131781 | LCSC | 0.0219 | 40487 | 0.0219 | 0.1095 | 5
27 | 4 | NCE3400 | Q16,Q17,Q18,Q19 | SOT-23-3_L2.9-W1.6-P1.90-LS2.8-BR |  | NCE3400 | 无锡新洁能 | C113202 | LCSC | 0.0585 | 14145 | 0.234 | 1.17 | 20
28 | 1 | 10K | R1 | R1206 |  | RTAN1206BKE10K0 | Stackpole Elec | C346744 | LCSC | 0.5266 | 2241 | 0.5266 | 2.633 | 5
29 | 7 | 10K_R1206 | R2,R3,R4,R17,R18,R19,R20 | R1206 |  | RTAN1206BKE10K0 | Stackpole Elec | C346744 | LCSC | 0.5266 | 2241 | 3.6862 | 18.431 | 35
30 | 3 | 1K_R0603 | R5,R30,R31 | R0603 |  | RC0603JR-071KL | YAGEO | C14676 | LCSC |  |  |  | 0.11 | 15 | Buy 100 and keep it for future orders
31 | 5 | ARG03BTC1002 | R6,R110,R112,R113,R114 | R0603 | 10kΩ | ARG03BTC1002 | Viking(光颉) | C309083 | LCSC | 0.0197 | 351620 | 0.0985 | 0.4925 | 25
32 | 1 | 100K | R8 | R0603 |  | RC0603FR-07100KL | YAGEO | C14675 | LCSC |  |  |  | 0.1 | 5 | Buy 100 and keep it for future orders
33 | 1 | 1K | R21 | R0603 |  | RC0603JR-071KL | YAGEO | C14676 | LCSC |  |  |  | 0.11 | 5 | Buy 100 and keep it for future orders
34 | 2 | 10K_R0603 | R32,R33 | R0603 |  | RC0603FR-0710KL | YAGEO | C98220 | LCSC |  |  |  | 0.1 | 10 | Buy 100 and keep it for future orders
35 | 1 | 5.1K | R34 | R0603 |  | RS-03K5101FT | Guangdong Fenghua Advanced Tech | C156350 | LCSC | 0.0008 | 191900 | 0.0008 | 0.004 | 5
36 | 1 | 5.1K_R0603 | R35 | R0603 |  | RS-03K5101FT | Guangdong Fenghua Advanced Tech | C156350 | LCSC | 0.0008 | 191900 | 0.0008 | 0.004 | 5
37 | 1 | CR1206F41005G | R92 | R1206 | 10MΩ | CR1206F41005G | LIZ(丽智电子) | C102064 | LCSC | 0.0042 | 2200 | 0.0042 | 0.021 | 5
38 | 4 | 0603WAF4702T5E | R99,R100,R101,R102 | R0603 | 47kΩ | 0603WAF4702T5E | UNI-ROYAL(厚声) | C25819 | LCSC |  |  |  | 0.11 | 20 | Buy 100 and keep it for future orders
39 | 4 | 0603WAF1101T5E | R103,R104,R105,R106 | R0603 | 1.1kΩ | 0603WAF1101T5E | UNI-ROYAL(厚声) | C22764 | LCSC |  |  |  | 0.1 | 20 | Buy 100 and keep it for future orders
40 | 2 | 0805W8F220JT5E | R107,R108 | R0805 | 22Ω | 0805W8F220JT5E | UNI-ROYAL(厚声) | C17561 | LCSC |  |  |  | 0.18 | 10 | Buy 100 and keep it for future orders
41 | 1 | 0603WAF6200T5E | R115 | R0603 | 620Ω | 0603WAF6200T5E | UNI-ROYAL(厚声) | C23220 | LCSC |  |  |  | 0.11 | 5 | Buy 100 and keep it for future orders
42 | 1 | IP2721_MAX12 | U3 | TSSOP-16_L5.0-W4.4-P0.65-LS6.4-BL |  | IP2721 MAX12 | INJOINIC | https://item.taobao.com/item.htm?spm=a21n57.1.0.0.4df9523cnwBY6a&id=688842211290&ns=1&abbucket=0&mt= | TAOBAO |  |  |  | 2.8 | 5 | PLEASE SELECT MAX12 version
43 | 1 | SPX3819M5-L-3-3/TR | U5 | SOT-23-5_L3.0-W1.7-P0.95-LS2.8-BR |  | SPX3819M5-L-3-3/TR | EXAR | C9055 | LCSC |  |  |  | 0.81 | 5
44 | 1 | ESP32-S | U7 | WIRELM-SMD_ESP32-S |  | ESP32-S | Ai-Thinker | https://detail.tmall.com/item.htm?abbucket=0&id=674729846391&ns=1&spm=a21n57.1.0.0.4df9523cnwBY6a | TMALL | 3.7721 |  |  | 7.1 | 5
46 | 1 | AP63205WU-7 | U32 | TSOT-23-6_L2.9-W1.6-P0.95-LS2.8-BL |  | AP63205WU-7 | DIODES(美台) | https://item.taobao.com/item.htm?spm=a1z0d.6639537/tb.1997196601.4.6daf7484fOMDHd&id=709423154281 | TAOBAO |  |  |  | 2.82 | 5
47 | 1 | TLC59108IPWR | U41 | TSSOP-20_L6.5-W4.4-P0.65-LS6.4-BL | - | TLC59108IPWR | TI(德州仪器) | C130031 | LCSC | 1.7994 | 1938 | 1.7994 | 8.997 | 5
48 | 1 | LMP7717MF/NOPB | U42 | SOT-23-5_L3.0-W1.7-P0.95-LS2.8-BL |  | LMP7717MF/NOPB | TI(德州仪器) | C202279 | LCSC | 2.1844 | 1003 | 2.1844 | 10.922 | 5
49 | 1 | TMUX1309BQBR | U44 | DHVQFN-16_L3.5-W2.5-P0.50-BL-EP |  | TMUX1309BQBR | TI(德州仪器) | C2871838 | LCSC | 0.2689 | 440 | 0.2689 | 1.3445 | 5
50 | 1 | TMUX1308QBQBRQ1 | U45 | QFN-16_L3.5-W2.5-P0.50-BL-EP |  | TMUX1308QBQBRQ1 | TI(德州仪器) | C2861017 | LCSC | 0.2861 | 2765 | 0.2861 | 1.4305 | 5
51 | 1 | CP2102N-A02-GQFN28R | U47 | QFN-28_L5.0-W5.0-P0.50-TL-EP3.3 |  | CP2102N-A02-GQFN28R | SILICON LABS(芯科) | C964632 | LCSC | 2.1351 | 2745 | 2.1351 | 10.6755 | 5
52 | 1 | ADS1115IDGSR | U48 | MSOP-10_L3.0-W3.0-P0.50-LS5.0-BL |  | ADS1115IDGSR | TI(德州仪器) | C37593 | LCSC | 3.39 | 3337 | 3.39 | 16.95 | 5
53 | 1 | U262-161N-4BVC11 | USB1 | USB-3.1-SMD_U262-161N-4BVC11 |  | U262-161N-4BVC11 | XKB Connectivity(中国星坤) | C319148 | LCSC | 0.4026 | 9561 | 0.4026 | 2.013 | 5
 |  |  |  |  |  |  |  |  |  |  |  | TOTAL | 143.96

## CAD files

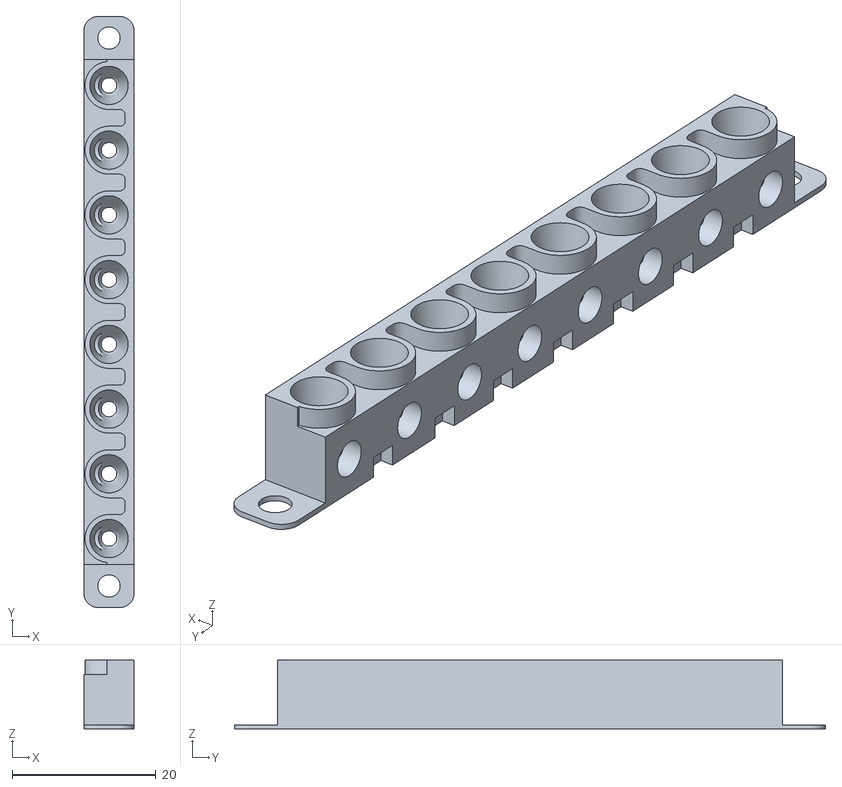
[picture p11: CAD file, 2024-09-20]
Production/3D models/[Aluminum] Tube holder.stl
7.00 x 82.2 x 9.54

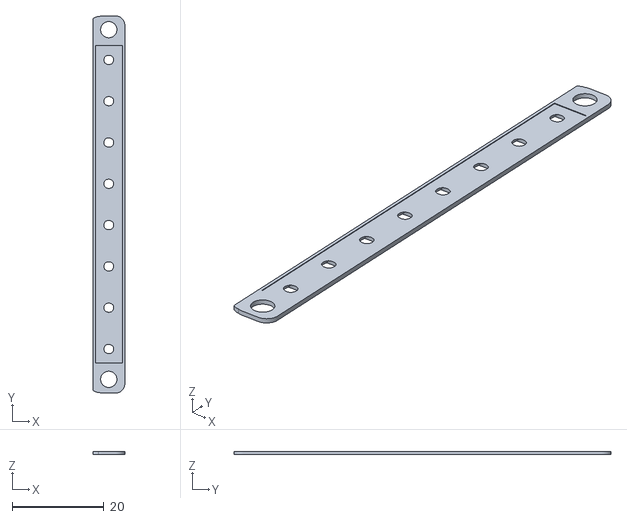
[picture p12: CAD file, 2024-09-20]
Production/3D models/[PETG] Intermediate part.stl
6.90 x 82.2 x 0.71

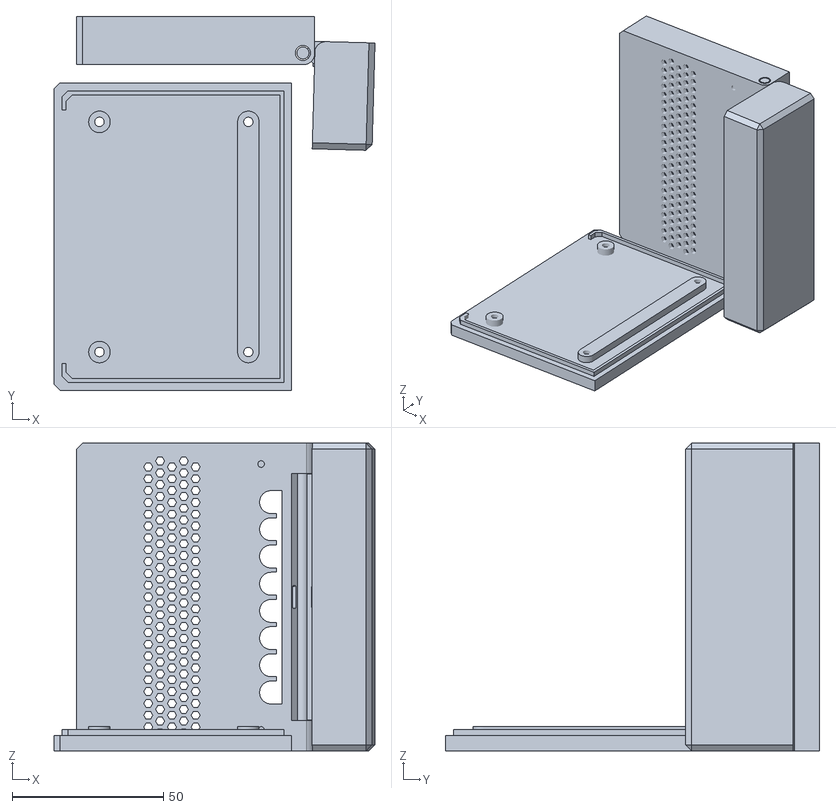
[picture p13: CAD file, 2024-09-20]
Production/3D models/[PLA] Case.stl
106.2 x 123.8 x 101.8

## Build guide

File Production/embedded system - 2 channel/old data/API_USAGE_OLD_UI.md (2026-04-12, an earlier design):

# Old UI API Usage Map

This file documents how the legacy frontend in `old data/` used the embedded GET API.

## Startup sequence (automatic)

1. `GET /OnGoing`
- Trigger: immediately when `data_query.js` loads (`isProtocolOngoing()`).
- Purpose: detect if an experiment is already running.

2. `GET /cycle_time`
- Trigger: inside `isProtocolOngoing()` after `/OnGoing` response.
- Purpose: initialize cycle period input and polling interval.

3. `GET /weights`
- Trigger: inside `isProtocolOngoing()`.
- Purpose: populate weights table.

4. `GET /lid_temp`
- Trigger: inside `isProtocolOngoing()`.
- Purpose: initialize lid temperature setting.

5. `GET /lid_diff`
- Trigger: inside `isProtocolOngoing()`.
- Purpose: initialize lid temperature delta setting.

6. `GET /melting_step`
- Trigger: inside `isProtocolOngoing()`.
- Purpose: initialize melting step.

7. `GET /melting_time`
- Trigger: inside `isProtocolOngoing()`.
- Purpose: initialize melting step duration.

8. `GET /melting_range`
- Trigger: inside `isProtocolOngoing()`.
- Purpose: initialize melting range sliders.

9. `GET /free_memory`
- Trigger: inside `isProtocolOngoing()`.
- Purpose: initialize memory usage bar.

10. `GET /protocols`
- Trigger: `window.onload` in `functions.js`.
- Purpose: load protocol library list.

11. `GET /device-config`
- Trigger: `DOMContentLoaded` in `index.html`.
- Purpose: populate device config bar (`ip`, `mdns`, `ssid`, `password`).

## Run control

1. `GET /manual_cycle`
- Trigger: click `#cycle` button.
- Follow-up: after ~3s, `updateData()` is called.

2. `GET /Run?degrees=<target>`
- Trigger: click `#temp` when button text is `Run`.
- Follow-up: on `[OK]`, starts `setInterval(updateData, CYCLE_TIME)`.

3. `GET /RunMelting`
- Trigger: click `#temp` when button text is `Run Melting Curve`.
- Follow-up: on `[OK]`, starts `setInterval(updateData, CYCLE_TIME)`.

4. `GET /Stop`
- Trigger: click `#temp` when button text is `Stop`.
- Follow-up: polling interval cleared.

## Data polling

1. `GET /data_request`
- Trigger: `updateData(false)` during active run.
- Timing: periodic interval (`CYCLE_TIME`).

2. `GET /last_run_request`
- Trigger: `updateData(true)` from `#last_run_load` click.

## Calibration signal flow (button `#calibrate_signal`)

1. `GET /ReadFluo`
- Trigger: calibration flow start.

2. `GET /fluo`
- Trigger: after ~10s delay post `/ReadFluo`.

3. `GET /Calibration`
- Trigger: after initial fluorescence is read.

4. `GET /readWeights`
- Trigger: after ~60s delay.

5. `GET /ReadFluo`
- Trigger: second pass after weights.

6. `GET /fluo`
- Trigger: after ~10s delay in second pass.

## Settings updates (UI button actions)

1. `GET /cycle_time?set=<ms>`
- Trigger: click `#cycle-time-set`.

2. `GET /lid_temp?set=<temp>`
- Trigger: click `#lid-temp-set`.

3. `GET /lid_diff?set=<delta>`
- Trigger: click `#lid-diff-set`.

4. `GET /step_temp?set=<temp>`
- Trigger: one `set_step_temp` implementation.
- Note: overridden by a later function with same name.

5. `GET /melting_step?set=<temp>`
- Trigger: effective `set_step_temp` implementation used at runtime.

6. `GET /melting_time?set=<ms>`
- Trigger: click `#melting-step-time-set`.

7. `GET /melting_range?set=<left,right>`
- Trigger: click `#melting-range-set`.

## Protocol management

1. `GET /protocols`
- Trigger: load protocol library on startup.

2. `GET /protocols?save_new=1&name=<name>&protocol_data=<json>`
- Trigger: click `#save-protocol`.

3. `GET /protocols?delete=1&name=<name>`
- Trigger: click delete icon in protocol list.

## Notes for migration

- The old UI uses GET for both reads and writes.
- Several writes are query-string based (`?set=...`).
- The runtime `set_step_temp` symbol is duplicated; the second definition (using `/melting_step`) wins in browser execution.

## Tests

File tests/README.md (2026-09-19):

# Production tests

These tests use a real qByte. Keep it empty and supervised while its heaters are on.

## Install

Run this from Windows or a machine that can open `http://qByte.local`:

```bash
python -m pip install -r tests/requirements.txt
python -m playwright install chromium
```

Use another device address when mDNS is unavailable. In PowerShell:

```powershell
$env:QBYTE_URL = "http://192.168.1.50"
```

## Run

```bash
python -m pytest tests/test_temperature_protocol.py -s
python -m pytest tests/test_ota_atomic.py -s
```

The temperature test uses the web interface to set the wells to 60 °C, the lid to 70 °C, and the lid difference to 10 °C. It reads all four sensors twice, ten seconds apart, then stops the protocol and restores the previous lid settings.

The OTA test is intended for release acceptance. It checks that the partition table has two application slots and runs the device transition only when the online manifest contains a newer version. It verifies the candidate image before starting, then accepts only the complete old or new firmware version until the new version boots.

## OTA power-cut test

Run this only while you are beside the qByte. A newer firmware version must already be published:

```powershell
$env:QBYTE_POWER_CUT = "1"
python -m pytest tests/test_ota_power_cut.py -s
```

The test asks before starting the OTA, tells you when to cut power, detects that the qByte has disappeared, and then asks you to reconnect it. Passing means the device boots a complete old or new firmware, remains stable, and serves all interface files. It cannot prove that power was physically removed, so it asks you to confirm that step.

All device requests use HTTP GET only.

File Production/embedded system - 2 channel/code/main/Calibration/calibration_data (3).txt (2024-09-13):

{"metal_resistance":["1.46","1.02","1","0.97","2.69","2.52","2.39","2.37","1.62","1.62"],"chamber_resistance":["2.21","1.85","1.81","1.76","3.48","2.89","2.57","2.52","2.23","2.2"],"real_temp":["73","83.3","83.6","84.3","57.1","59.4","61.5","63","72","71.3"]}

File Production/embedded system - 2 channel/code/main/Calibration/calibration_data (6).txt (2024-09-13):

{"heater1_resistance":["2.25","2.25","1.16","1.12","0.55","0.53"],"heater2_resistance":["2.23","2.23","1.15","1.14","0.55","0.53"],"heater3_resistance":["2.24","2.24","1.14","1.17","0.57","0.55"],"lid_resistance":["7.65","7.65","7.33","7.25","4.88","4.82"],"chamber_resistance":["2.48","2.51","2.23","2.22","2.14","2"],"real_temp":["47.15","49.45","57","58","65","70"]}

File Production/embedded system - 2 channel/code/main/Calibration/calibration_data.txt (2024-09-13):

{"chamber_resistance":["5.68","5.64","5.15","4.17","4.02","3.65","3.49","3.41","3.35","3.27","4.25","4.43","4.57"],"measured_resistance":["5.19","5.18","1.92","1.96","1.97","1.21","1.21","1.21","1.21","1.21","3.52","3.52","3.51"],"real_temp":["37.0","36.9","67.8","63.7","63.6","77.5","76.7","76.5","76.4","76.2","44.3","44.5","48"]}

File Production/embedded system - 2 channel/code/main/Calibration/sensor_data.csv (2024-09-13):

temperature | resistance | replicate
38.75 | 5.5 | 1
52.8 | 3.166 | 1
67.5 | 1.891 | 1
39.3 | 5.44 | 2
53.5 | 3.141 | 2
67.5 | 1.899 | 2
38.7 | 5.45 | 3
53.6 | 3.136 | 3
67.9 | 1.885 | 3

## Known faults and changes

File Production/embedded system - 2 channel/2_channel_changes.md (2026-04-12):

# 2-Channel System Changes & Implementation Plan

## Hardware & Pin Updates
- [ ] **Microcontroller**: ESP32S3 Dev Module
- [x] **Heater PWM Pins** (Updated in `main.ino`):
  - PWM_1: 33
  - PWM_2: 34
  - PWM_3: 35
  - PWM_LID: 36
- [ ] **I2C Bus**:
  - SDA: Pin 3
  - SCL: Pin 2
- [ ] **RGB LEDs (TLC59108)**: Independent brightness parameters per color setup at max intensity initially.
  - Blue: I2C `0x40`
  - Red: I2C `0x41`
  - Green: I2C `0x42`
- [ ] **Multiplexer (MUX)**:
  - SW1: Pin 5
  - SW2: Pin 6
  - SW3: Pin 7

## Sensor Reading (2 Diodes)
- [ ] Channel 1: Reads as before via MUX (`ADC AIN1`).
- [ ] Channel 2: Reads simultaneously via MUX (`ADC AIN3`).
- [ ] **Auto-gain Handling**: 48 independent auto-gain trackers (8 tubes * 3 colors * 2 channels) implemented.

## Cycle & Data Storage
- [ ] **Configuration (`config.txt`)**: Set up mapped color filters for each channel (e.g., JAS Green, 105 ORANGE) to be selected in UI. Assign default LED brightness intensities here as well.
- [ ] **Cycle Sequence**: For each of the 8 tubes, iterate through 3 light channels (Blue, Red, Green). At each step, read both photodiodes (AIN1, AIN3).
- [ ] **Storage Format**: Store a standardized set of 48 values per read cycle into the CSV format.
- [ ] **Peripheral Code Adaptation**: Refactor small commands like `led_trial` to independently test each LED and color sequentially.

## User Interface (`/code/main/data`)
- [ ] **Data Parsing**: Adapt JS CSV parsing for the new 48-variable structure.
- [ ] **Graph Display**: Update charts so the center of the point reflects the color of the channel, while the point's border identifies the sample.
- [ ] **Analysis Tab Tools**:
  - [ ] Allow viewing data from any combination of Light (LED color) + Diode.
  - [ ] Retain current normalization selections.
  - [ ] Introduce cross-channel normalization math (e.g., divide Blue Light Diode 1 by Red Light Diode 2).

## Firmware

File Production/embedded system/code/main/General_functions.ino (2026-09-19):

void Initialize() {

  Serial.begin(115200);
  delay(500); //To give the serial port time to start up

  Wire.begin();

  if(!SPIFFS.begin()){
    Serial.println("[ERROR] An Error has occurred while mounting SPIFFS");
    return;
  }

  loadConfig();
 
  esp32FOTA.setManifestURL(UPDATE_BASE_URL + "/update_server/data/fota.json");

    //config.mDNS to char*
  char mDNS[config.mDNS.length() + 1];
  config.mDNS.toCharArray(mDNS, config.mDNS.length() + 1);

  //Initialize the mDNS in config.mDNS
  if (!MDNS.begin(mDNS)) {
    Serial.println("[ERROR] Error setting up MDNS responder!");
  }
 
  Serial.println("mDNS: " + config.mDNS);
  Serial.println("VERSION: " + String(config.VERSION));

  //Initialize the LEDs
  if (config.VERSION == 1) {
    FastLED.addLeds<WS2812B, DATA_PIN, RGB>(leds, NUM_LEDS).setCorrection(UncorrectedColor);
  } else {
    leds2.init(); // Initialize the TLC59108
    leds2.setRegister(0x11,  0x00); // Set general address to 0
    leds2.setLedOutputMode(TLC59108::LED_MODE::PWM_IND);
  }


  PD_array.setGain(GAIN_SIXTEEN);  
  PD_array.begin(0x48);


  //PWM pins as an output and initilize them
  pinMode(PWM_1, OUTPUT);
  pinMode(PWM_2, OUTPUT);
  pinMode(PWM_3, OUTPUT);
  pinMode(PWM_LID, OUTPUT);

  digitalWrite(PWM_1, LOW);
  digitalWrite(PWM_2, LOW);
  digitalWrite(PWM_3, LOW);
  digitalWrite(PWM_LID, LOW);

  //myPID.SetOutputLimits(0,255);
  PWM_PID_1.SetSampleTime(PID_SAMPLE);
  PWM_PID_2.SetSampleTime(PID_SAMPLE);
  PWM_PID_3.SetSampleTime(PID_SAMPLE);
  PWM_PID_LID.SetSampleTime(PID_SAMPLE);

  if (config.VERSION >= 2)
  {
    PWM_PID_LID.SetOutputLimits(0,255); // set maximun value of LID to 125
    PWM_PID_1.SetOutputLimits(0,125);
    PWM_PID_2.SetOutputLimits(0,125);
    PWM_PID_3.SetOutputLimits(0,125);
  } else {
    PWM_PID_LID.SetOutputLimits(0,255); // set maximun value of LID to 255
    PWM_PID_1.SetOutputLimits(0,255);
    PWM_PID_2.SetOutputLimits(0,255);
    PWM_PID_3.SetOutputLimits(0,255);
  }

  PWM_PID_1.Start(calculate_temperature(WELL1),0,0);
  PWM_PID_2.Start(calculate_temperature(WELL2),0,0);
  PWM_PID_3.Start(calculate_temperature(WELL3),0,0);
  PWM_PID_LID.Start(calculate_temperature(LID),0,0);


  pinMode(SW1, OUTPUT);
  pinMode(SW2, OUTPUT);
  pinMode(SW3, OUTPUT);
  pinMode(SW4, OUTPUT);

  serverBegin();
  manage_reset();

  Serial.println("[INFO] Initialization complete");
  

}

void manage_reset() {

  // read the last line of last_run.txt
  if (!SPIFFS.exists("/last_run.txt")) {
    Serial.println("[WARNING] last_run.txt file don't exist. If this is your first run, please ignore this warning.");
    return;
  }

  File f = SPIFFS.open("/last_run.txt", "r+");
  String last_line = ""; // to save last line of last_run.txt
  String buffer = f.readStringUntil('\n'); // to read the last line of last_run.txt

  //Otherwise we continue reading until the last line
  while (f.available() && (buffer.length() > 3)) { 
    last_line = buffer;  
    buffer = f.readStringUntil('\n');
  }
  f.close();

  // debug last line split
  if (config.DEBUG)
  {
    Serial.print("[DEBUG] last line: ");
    Serial.println(buffer);
    Serial.println();
  }

  if (buffer.indexOf("stop") == -1) {
    Serial.println("[WARNING] A protocol was interrupted. Re-starting the protocol.");

    //count the "," in last_line
    int count = 0;
    for (int i = 0; i < last_line.length(); i++) {
      if (last_line.charAt(i) == ',') {
        count++;
      }
    }

    //If the file is empty we return an error
    if (count == 0) {
      Serial.println("[WARNING] last_run.txt file is empty. That may indicate a problem saving the last data");
      
      //Cancel the run
      OnGoing = false;

      //write on last_run.txt "stop" and close the file
      f.println("stop");
      f.close();
      return;
    }

    // split last line values by ","
    String last_line_split[count+1];

    int i = 0;
    for (int j = 0; j < last_line.length(); j++) {
      if (last_line.charAt(j) == ',') {
        i++;
      } else {
        last_line_split[i] += last_line.charAt(j);
      }
    }

    time_before_interruption = (long int)last_line_split[0].toInt();
    
    OnGoing = true;
    start_time = millis();

    heater_goal = (float)last_line_split[1].toFloat();
    
    Serial.println("[INFO] Heater new target: " + String(heater_goal) + "ºC");

    PWM_PID_1.Start(calculate_temperature(WELL1),PWM_PID_1.Run(heater_goal),heater_goal);
    PWM_PID_2.Start(calculate_temperature(WELL2),PWM_PID_2.Run(heater_goal),heater_goal);
    PWM_PID_3.Start(calculate_temperature(WELL3),PWM_PID_3.Run(heater_goal),heater_goal);
    PWM_PID_LID.Start(calculate_temperature(LID),PWM_PID_LID.Run(config.LID_TEMP),config.LID_TEMP);

    // Continue with the protocol file
    File f = SPIFFS.open("/last_run.txt", "a+");
    f.close();

    return;
  }
}

void runPID() {
  if (OnGoing)
  {
    int TEMP_PID_1 = calculate_temperature(WELL1);
    int TEMP_PID_2 = calculate_temperature(WELL2);
    int TEMP_PID_3 = calculate_temperature(WELL3);
    int TEMP_PID_LID = calculate_temperature(LID);

    DATA_PID_LID = PWM_PID_LID.Run(TEMP_PID_LID);
    analogWrite(PWM_LID, DATA_PID_LID);

    //We wait for the LID to be hot to heat the wells
    if (sq(config.LID_TEMP - TEMP_PID_LID) < sq(config.LID_DIFFERENCE))
    {
      DATA_PID_1 = PWM_PID_1.Run(TEMP_PID_1);
      DATA_PID_2 = PWM_PID_2.Run(TEMP_PID_2);
      DATA_PID_3 = PWM_PID_3.Run(TEMP_PID_3);
      analogWrite(PWM_1, DATA_PID_1);
      analogWrite(PWM_2, DATA_PID_2);
      analogWrite(PWM_3, DATA_PID_3);
    } else {
      analogWrite(PWM_1, 0);
      analogWrite(PWM_2, 0);
      analogWrite(PWM_3, 0);
    }
  } else {
    analogWrite(PWM_1, 0);
    analogWrite(PWM_2, 0);
    analogWrite(PWM_3, 0);
    analogWrite(PWM_LID, 0);
  }
  
}

char** loadCredentials() {
  String ssid;
  String password;

  if (SPIFFS.exists("/credentials.txt")) {
    File file = SPIFFS.open("/credentials.txt", "r");
    if (file) {
      ssid = file.readStringUntil(',');
      password = file.readStringUntil('\r');
      file.close();
    } else {
      Serial.println("[ERROR] Could not open credentials.txt");
    }
  } else {
    Serial.println("[WARNING] credentials.txt does not exist");
  }

  // Always return two valid strings so first-run AP mode can safely test for
  // an empty SSID. Callers own the returned strings and array.
  char** result = new char*[2];
  result[0] = new char[ssid.length() + 1];
  result[1] = new char[password.length() + 1];
  strcpy(result[0], ssid.c_str());
  strcpy(result[1], password.c_str());
  return result;
}

void loadConfig(){
  if (SPIFFS.exists("/config.txt")) {
    File file = SPIFFS.open("/config.txt", "r");

    if (file) 
    {
      // load the file as a JSON

      String json_string = file.readString();
      file.close();

      // parse it as a json
      DynamicJsonDocument json(1024);
      deserializeJson(json, json_string);
      // -------------------------------------- VERSION -----------------------------------
      config.VERSION = json["version"].as<int>();

      //-------------------------------------- mDNS -----------------------------------

      // load the mDNS name
      
      config.mDNS = json["mDNS"].as<String>();
      

      //----------------------------------- CYCLE_TIME --------------------------------
      
      config.CYCLE_TIME = json["cycle_time"].as<unsigned int>();

      //----------------------------------- LOAD WEIGHTS --------------------------------

      //get the weights as a string
      String weights = json["weights"].as<String>();

      //separate the weights by ","
      int count = 0;
      for (int i = 0; i < weights.length(); i++) {
        if (weights.charAt(i) == ',') {
          count++;
        }
      }

      //split the weights by ","
      String weights_split[count+1];

      int i = 0;
      for (int j = 0; j < weights.length(); j++) {
        if (weights.charAt(j) == ',') {
          i++;
        } else if  (weights.charAt(j) != '[' and weights.charAt(j) != ']') {
          weights_split[i] += weights.charAt(j);
        }
      }
      //convert the weights to float
      for (int j = 0; j < count+1; j++) {
        config.WEIGHTS[j] = (float)weights_split[j].toFloat();
      }

      // ----------------------------------- LOAD LID TEMPERATURE AND DIFF --------------------------------

      config.LID_TEMP = json["lid_temp"].as<float>();
      config.LID_DIFFERENCE = json["lid_difference"].as<float>();

      // ----------------------------------- LOAD MELTING CURVE VALUES --------------------------------
      
      config.MELTING_STEP = json["melting_step"].as<float>();
      config.MELTING_TIME = json["melting_time"].as<unsigned int>();

      // get the melting range as a string
      String melting_range = json["melting_range"].as<String>();
            
      //separate the melting range by ","
      count = 0;
      for (int i = 0; i < melting_range.length(); i++) {
        if (melting_range.charAt(i) == ',') {
          count++;
        }
      }

      //split the melting range by ","
      String melting_range_split[count+1];

      i = 0;
      for (int j = 0; j < melting_range.length(); j++) {
        if (melting_range.charAt(j) == ',') {
          i++;
        } else if  (melting_range.charAt(j) != '[' and melting_range.charAt(j) != ']') {
          melting_range_split[i] += melting_range.charAt(j);
        }
      }
      //convert the melting range to float
      for (int j = 0; j < count+1; j++) {
        config.MELTING_RANGE[j] = (float)melting_range_split[j].toFloat();
      }

      // adjust melting temp variable to the first value of the melting range
      melting_temp = config.MELTING_RANGE[0];
      // ---------------------------------- DEBUG -------------------------------------
      
      if (json["debug"] == true) {
        config.DEBUG = true;
      } else {
        config.DEBUG = false;
      }

      // Keep the selected interface theme across restarts. Older config files
      // do not contain this key and therefore retain the Tokyo Night default.
      if (json.containsKey("theme")) {
        config.THEME = json["theme"].as<String>();
      }
      
      if (config.DEBUG == true) {
        Serial.println("[DEBUG] Config file content: " + json_string);
      }


    } else {
      Serial.println("[ERROR] Problem loading configuration file");
    }

  } else {
    Serial.println("[ERROR] Problem loading configuration file");
  }
}

void saveConfig(){
  DynamicJsonDocument json(1024);

  // save the version
  json["version"] = config.VERSION;

  // save mDNS name
  json["mDNS"] = config.mDNS;
  json["cycle_time"] = config.CYCLE_TIME;
  json["debug"] = config.DEBUG;
  json["theme"] = config.THEME;

  String weights_string = "[";
  for (int i=0;i<8;i++){
    weights_string += config.WEIGHTS[i];
    if (i != 7) {
      weights_string += ",";
    }
  }
  weights_string += "]";

  json["weights"] = weights_string;
  json["lid_temp"] = config.LID_TEMP;
  json["lid_difference"] = config.LID_DIFFERENCE;

  String melting_range_string = "[" + String(config.MELTING_RANGE[0]) + "," + String(config.MELTING_RANGE[1]) + "]";

  json["melting_range"] = melting_range_string;
  json["melting_step"] = config.MELTING_STEP;
  json["melting_time"] = config.MELTING_TIME;
  
  // Serial.println("[DEBUG] Config file content: " + json.as<String>());

  File file = SPIFFS.open("/config.txt", "w");
  if (file) {
    serializeJson(json, file);
    file.close();
  } else {
    Serial.println("[ERROR] Problem saving configuration file");
  }
}

void saveCredentials (String ssid, String password)
{
  File file = SPIFFS.open("/credentials.txt", "w+");
  if (file) {
    //erase all the content in the file
    file.seek(0);
    // write the credentials
    file.print(ssid);
    file.print(",");
    file.println(password);
    file.close();
  } else {
    Serial.println("[ERROR] Problem saving credentials");
  }
}
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

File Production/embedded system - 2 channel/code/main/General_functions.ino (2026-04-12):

extern volatile bool force_manual_cycle;

void disable_tlc_allcall(uint8_t addr) {
  // Read MODE1 register (0x00)
  Wire.beginTransmission(addr);
  Wire.write(0x00);
  Wire.endTransmission();

  Wire.requestFrom((int)addr, 1);
  if (!Wire.available()) {
    return;
  }

  uint8_t mode1 = Wire.read();
  mode1 &= ~0x01; // Clear ALLCALL bit (bit 0)

  // Write MODE1 back with ALLCALL disabled
  Wire.beginTransmission(addr);
  Wire.write(0x00);
  Wire.write(mode1);
  Wire.endTransmission();
}

void Initialize() {

  Serial.begin(115200);
  delay(500); //To give the serial port time to start up

  Wire.begin(3, 2); // SDA=3, SCL=2

  if(!SPIFFS.begin()){
    Serial.println("[ERROR] An Error has occurred while mounting SPIFFS");
    return;
  }

  loadConfig();
 
  esp32FOTA.setManifestURL("https://" + UPDATE_SERVER + "/data/fota.json");
 
  Serial.println("[INIT] mDNS: " + config.mDNS);
  Serial.println("[INIT] VERSION: " + String(config.VERSION));

  // Initialize the 3 color LED drivers
  leds_blue.init();
  leds_red.init();
  leds_green.init();

  // Disable default ALLCALL response so each driver only answers to its own address.
  disable_tlc_allcall(0x40);
  disable_tlc_allcall(0x41);
  disable_tlc_allcall(0x42);

  leds_blue.setLedOutputMode(TLC59108::LED_MODE::PWM_IND);
  leds_red.setLedOutputMode(TLC59108::LED_MODE::PWM_IND);
  leds_green.setLedOutputMode(TLC59108::LED_MODE::PWM_IND);

  Serial.println("[INIT] LED initialized");

  PD_array.setGain(GAIN_SIXTEEN);  
  PD_array.begin(0x48);

  Serial.println("[INIT] Photodiodes initialized");

  //PWM pins as an output and initilize them
  pinMode(PWM_1, OUTPUT);
  pinMode(PWM_2, OUTPUT);
  pinMode(PWM_3, OUTPUT);
  pinMode(PWM_LID, OUTPUT);

  digitalWrite(PWM_1, LOW);
  digitalWrite(PWM_2, LOW);
  digitalWrite(PWM_3, LOW);
  digitalWrite(PWM_LID, LOW);

  //myPID.SetOutputLimits(0,255);
  PWM_PID_1.SetSampleTime(PID_SAMPLE);
  PWM_PID_2.SetSampleTime(PID_SAMPLE);
  PWM_PID_3.SetSampleTime(PID_SAMPLE);
  PWM_PID_LID.SetSampleTime(PID_SAMPLE);

  if (config.VERSION >= 2)
  {
    PWM_PID_LID.SetOutputLimits(0,255); // set maximun value of LID to 125
    PWM_PID_1.SetOutputLimits(0,125);
    PWM_PID_2.SetOutputLimits(0,125);
    PWM_PID_3.SetOutputLimits(0,125);
  } else {
    PWM_PID_LID.SetOutputLimits(0,255); // set maximun value of LID to 255
    PWM_PID_1.SetOutputLimits(0,255);
    PWM_PID_2.SetOutputLimits(0,255);
    PWM_PID_3.SetOutputLimits(0,255);
  }

  PWM_PID_1.Start(calculate_temperature(WELL1),0,0);
  PWM_PID_2.Start(calculate_temperature(WELL2),0,0);
  PWM_PID_3.Start(calculate_temperature(WELL3),0,0);
  PWM_PID_LID.Start(calculate_temperature(LID),0,0);

  Serial.println("[INIT] PWM initialized");

  pinMode(SW1, OUTPUT);
  pinMode(SW2, OUTPUT);
  pinMode(SW3, OUTPUT);
  pinMode(SW4, OUTPUT);

  serverBegin();
  manage_reset();

  Serial.println("[INIT] Initialization complete");
  

}
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

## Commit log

2024-09-13 General cleaning. Add BoM.
    [BoM.xlsx, sensor_data.csv]
2024-09-20 Update 3D models
    [[Aluminum] Tube holder.stl, [PETG] Intermediate part.stl, [PLA] Case.stl]
2024-09-20 Typo fixing
    [[Aluminum] Tube holder.stl, [PETG] Intermediate part.stl, [PLA] Case.stl]
2024-09-20 Upload gerbers
    [PCB BoM.xlsx, PickAndPlace_Centroid.xlsx]
2024-11-06 Updated Arduino IDE instructions
2025-01-08 Add adafruit unified sensor
2025-01-09 fix typo in the board manager
2025-03-12 fluorescence self calibration
2025-10-15 Added board installation links
2026-03-29 Add qByte embedded system (2-channel)
    Import full qByte production embedded system for the 2-channel device. Adds VSCode project configs, API documentation (MD and PDF), firmware binaries, Arduino source files (main, AP_Mode, calibration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
    [sensor_data.csv]
